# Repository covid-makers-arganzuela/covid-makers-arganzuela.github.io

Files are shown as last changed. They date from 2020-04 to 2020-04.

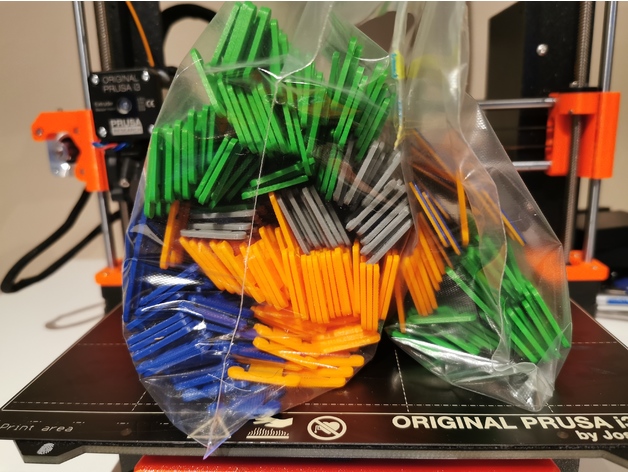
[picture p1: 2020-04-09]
modelos/salvaorejas/Surgical+Mask+Strap+Remix/images/IMG_20200330_075304.jpg

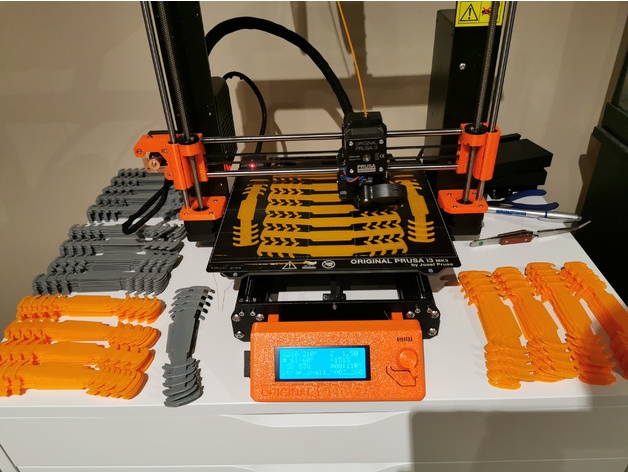
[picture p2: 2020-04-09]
modelos/salvaorejas/Surgical+Mask+Strap+Remix/images/IMG_20200330_213939.jpg

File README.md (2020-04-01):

# Grupo de Arganzuela de Coronavirus Makers

En este sitio mantenemos información útil para la coordinación del grupo de Arganzuela de [Coronavirus Makers](https://www.coronavirusmakers.org).

:tada: Canal de comunicación oficial: [grupo de Telegram](https://t.me/cov19arganzuela)

## Información de fabricación

* [Recomendaciones de ajustes de la impresora](ajustes.md): breve guía sobre
  cómo poner a punto la impresora antes de comenzar.

* [Modelos de visera](modelos/): modelos 3D de viseras utilizados por el grupo
  de Arganzuela. Dentro de los directorios se pueden encontrar configuraciones
  recomendadas para determinadas impresoras (archivos gcode y proyectos cuda
  personalizados).

## Colabora

Si tienes ajustes personalizados de impresión de alguno de los modelos puedes:
 * Si tienes permisos en este repositorio: 
   * haz el commit directamente
 * Si no tienes permisos en este repositorio o quires una revisión: 
   * haz una pull request en este repositorio
 * Si no sabes como hacer una pull request:
   * envía tus configuraciones (.gcode y proyecto Cura/Slicer .3MF/.MRML) al [grupo de Telegram](https://t.me/cov19arganzuela
)

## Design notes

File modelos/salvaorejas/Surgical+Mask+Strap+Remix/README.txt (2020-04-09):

Surgical Mask Strap Remix by Suraky on Thingiverse: https://www.thingiverse.com/thing:4249113

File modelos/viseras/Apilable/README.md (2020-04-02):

# Visera apilable (bescobarca)

Esta visera fue publicada por el usuario bescobarca en Thingverse. 

# Parámetros de impresión
Se recuerda que los parámetros pueden variar de unas impresoras a otras
 - Relleno: 60%
 - Soportes: no
 - Boquilla: 0.4 mm (**Es posible que no sirvan las de tamaño mayor**)
 - Material

# Licencia
Esta pieza se distribuye bajo una licencia CC-BY

# Enlaces
Pieza en Thingiverse: <https://www.thingiverse.com/thing:4251325>

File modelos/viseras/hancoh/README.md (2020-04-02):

# Visera Gregorio Marañón
Este modelo de visera es el disponible en la web de CoronavirusMakers. Su autor, como se indica en el PDF disponible, es  [Hanoch Hemmerich https://www.thingiverse.com/HanochH/about]

## Parámetros de impresión recomendados
Se recuerda que los parámetros pueden variar de unas impresoras a otras.

 - Diámetro del nozzle: 0.4mm
 - Altura de capa: 0.28mm
 - Relleno: 50%
 - Tipo de relleno: Rejilla
 - Capas superiores: 4
 - Capas inferiores: 2
 - Flujo: 80%
 - Sin soportes

 ### Velocidad de impresión:
 - Perímetros: 80mm/s
 - Perímetros pequeños: 80mm/s
 - Perímetros externos: 80mms/s
 - Relleno: 80mms/s
 - Relleno solido: 80mms/s
 - Relleno solido superior: 80mm/s
 - Puentes: 80mm/s
 - Relleno: 80mm/s
 - Recorrido: 180mm/s

 ### Material
  - PLA
 
 ## Enlaces
 - Publicación de la visera (zip): https://www.coronavirusmakers.org/index.php/es/documentos/category/7-d-i-y

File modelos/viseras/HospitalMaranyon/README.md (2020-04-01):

# Visera Gregorio Marañón
Este modelo de visera fue publicado por la Unidad de planificación avanzada y manufactura 3D del Hospital Gregorio Marañón, en su cuenta de twitter (@3d_maranon)

## Parámetros de impresión recomendados
 - Boquilla: 0.4mm a 0.8mm 
 - Altura de capa: 0.3mm 
 - Capas superiores e inferiores 3
 - Perímetros 3
 - Relleno 20%, triangular
 - Sin soporte
 - Velocidad de impresión: A elección del operador.
 
 ## Enlaces
 - Publicación de la visera: https://twitter.com/3d_maranon/status/1242177410759524355
 - Parámetros de impresión: https://twitter.com/3d_maranon/status/1242181121854582785

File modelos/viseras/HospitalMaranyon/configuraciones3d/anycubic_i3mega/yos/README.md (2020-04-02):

# Configuraciones

 - Temperatura capa inicial de la cama: 70
 - Temperatura capa inicial: 220
 - Velocidad capa inicial: 20 mm/s

Resto configuraciones por defecto

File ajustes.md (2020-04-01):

# Recomendaciones de ajustes de la impresora

(cortesía de Manel Ruiz)
 
En primer lugar, perded un poco de tiempo en ajustar la impresora, os evitará
dolores de cabez y tirar piezas a la basura (yo llevo unas cuantas). 
 
 * **Revisad la parte mecánica:** rodamientos, tensión de las correas de
   transmisión,... (hasta que apreté y ajusté bien todos los rodamientos,
   especialmente los de debajo de la cama, no desapareciero problemas que estaba
   intentando resolver cambiado ajustes SW) 
 
 * **Nivelación de la cama:** ha sido otro de mis grandes problemas. Revisadlo
   cada cierto tiempo si es necesario. 
 
 * **Calibrado:** hacedlo según se indica en
   https://covidmadrid.com/prueba-de-tolerancia/ Yo no lo hice del todo bien y
   he impreso unas cuantas visera cuya ranura es estrecha y no sé si podrá
   montarse la pantalla de PVC. Ahora tengo una expansión horizontal de -0,3 y
   queda de lujo. 
 
 * **Primera capa:** lo que mal empieza, mal acaba. Hasta que no he conseguido
   una buena primera capa todo han sido problemas. Lo que yo he hecho: 
   Subir la temperatura de la cama en la primera capa y después bajarla (ahora
   tengo 70º en la primera capa, 60º en el resto). Empecé con 75/70 y se pegaba
   bien la primera capa, pero después se abombaba la pared de la visera por el
   exceso de calor de la cama.  Subir la temperatura de impresión en la primera
   capa y después bajarla (yo ahora tengo 220º/215º) Bajar la velocidad de la
   primera capa. He terminado poniendo 20 mm/s para que la primera capa se fije
   bien a la cama. Resto de capas a 60 mm/s.

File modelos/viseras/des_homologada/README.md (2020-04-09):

# Visera del grupo covidmadrid

Estuvo homologada por la Comunidad de Madrid durante algunos días pero luego se
retiró la homologación. Dos tipos de impresión A (única) / B (partes) ambas con arandelas.

 * Ver ficha: https://covidmadrid.com/modelos-a-imprimir/
 
# Notas sobre la impresión

##Tetones para la parte frontal (Remache Frontal):
Probablemente necesitan escalado y ajustado

## Prueba de tolerancia
Se recomienda antes de imprimir el modelo realizar la prueba de tolerancia: https://covidmadrid.com/prueba-de-tolerancia/

## Ficheros STL
Para imprimir la visera hay dos opciones:
1. Imprimir el modelo A, que incluye la visera completa. Necesita una cama lo suficientemente grande. 
2. Imprimir el modelo B, que es el mismo que el modelo A, pero dividido en dos partes. Se deberá imprimir un fichero B1 y uno de los B2 (modelo con o sin hebilla). 

Independientemente de que se opte por imprimir el modelo A o el B, se necesiará también dos arandelas y los remaches que se consideren necesarios.

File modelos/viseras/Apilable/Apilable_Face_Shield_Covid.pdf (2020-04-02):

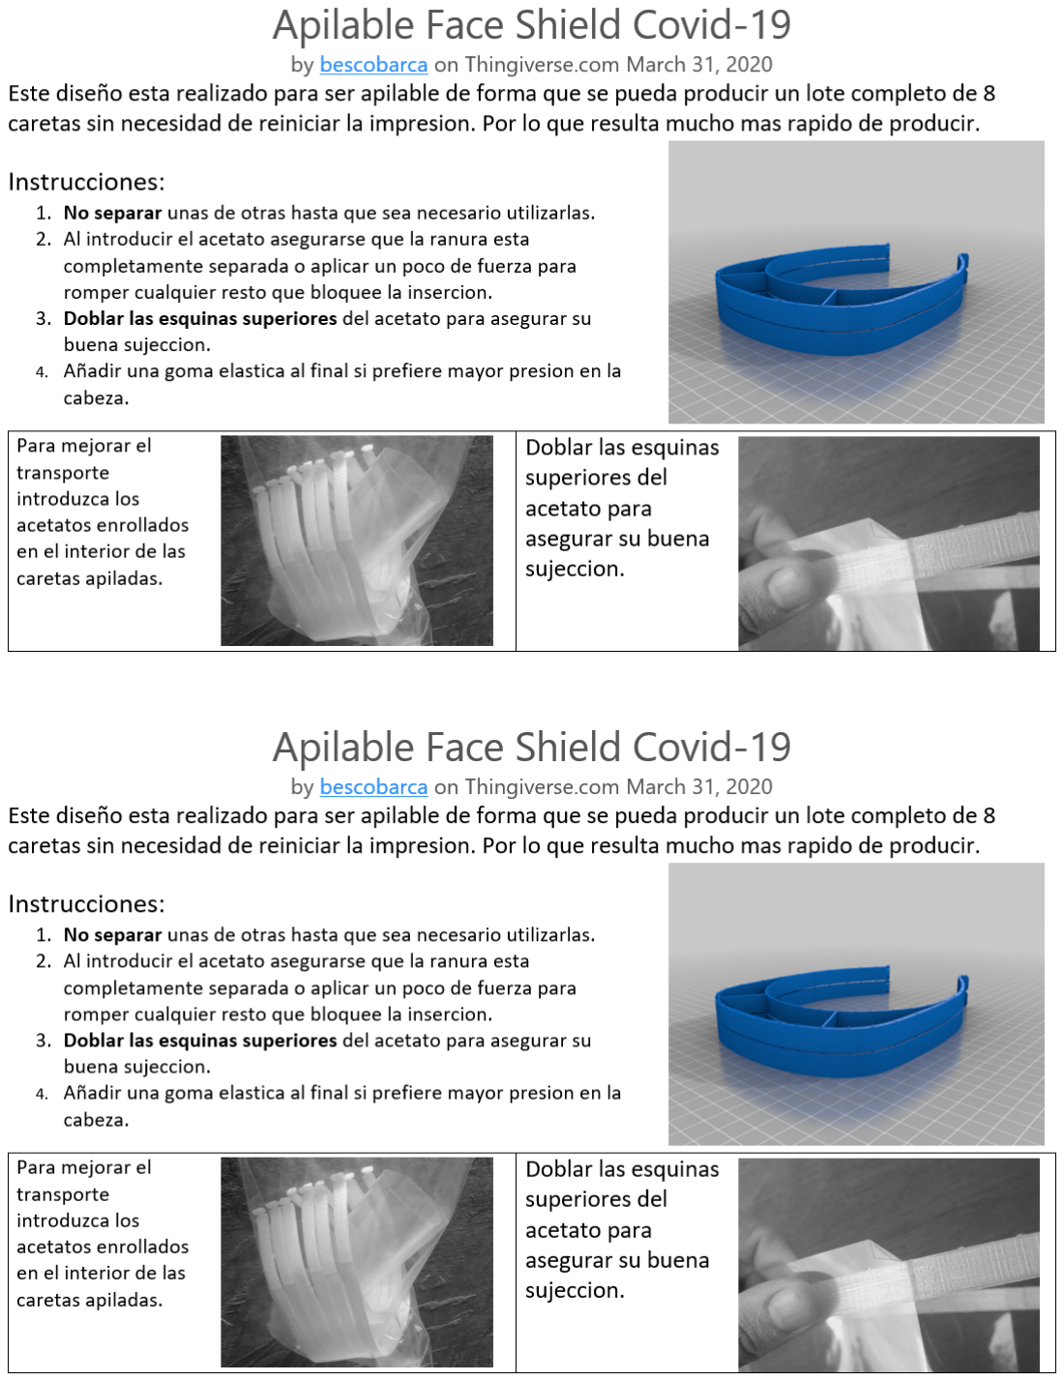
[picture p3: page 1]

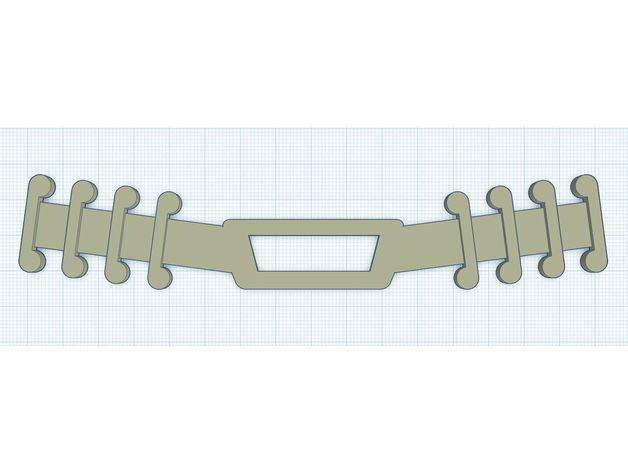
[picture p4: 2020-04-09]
modelos/salvaorejas/Surgical+Mask+Strap+Remix/images/strap-remix.JPG

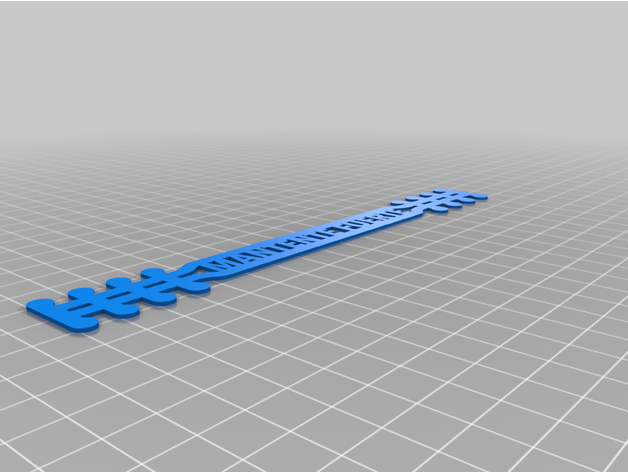
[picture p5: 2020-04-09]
modelos/salvaorejas/Salva+orejas+con+frases+/images/MANTENTE_FUERTE.png

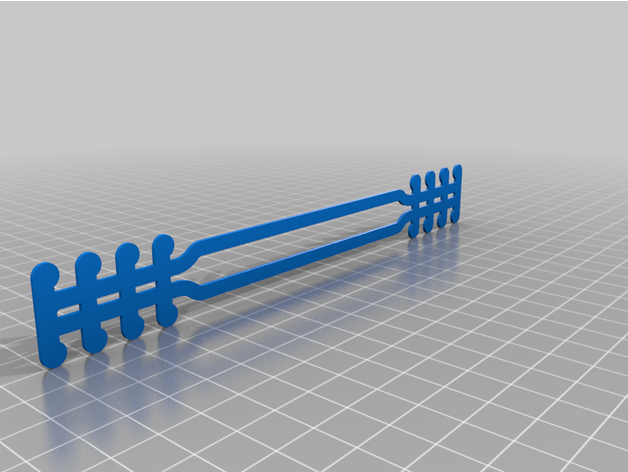
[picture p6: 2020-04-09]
modelos/salvaorejas/Salva+orejas+con+frases+/images/salva_orejas.png

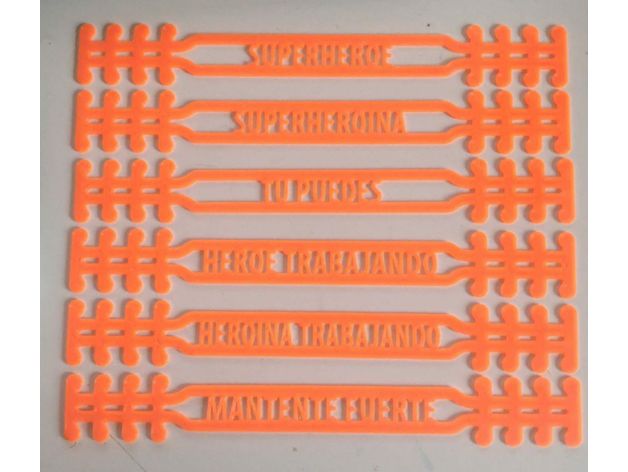
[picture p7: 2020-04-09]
modelos/salvaorejas/Salva+orejas+con+frases+/images/photo_2020-04-08_16.11.01.jpeg

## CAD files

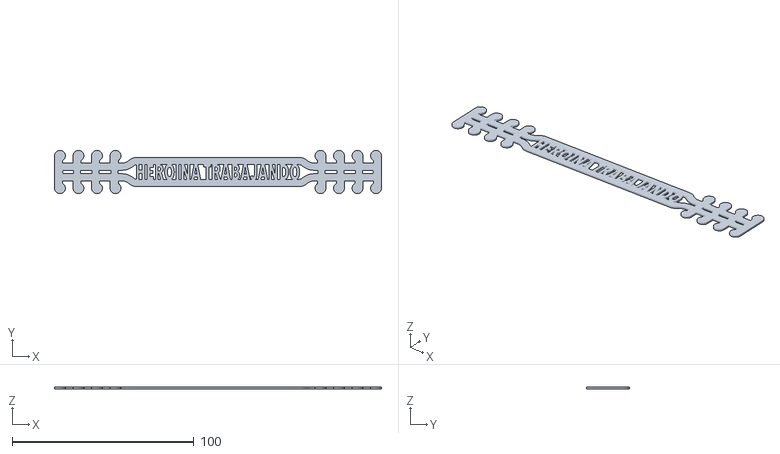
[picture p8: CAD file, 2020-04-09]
modelos/salvaorejas/Salva+orejas+con+frases+/files/HEROINA_TRABAJANDO.stl
180.0 x 23.8 x 1.00

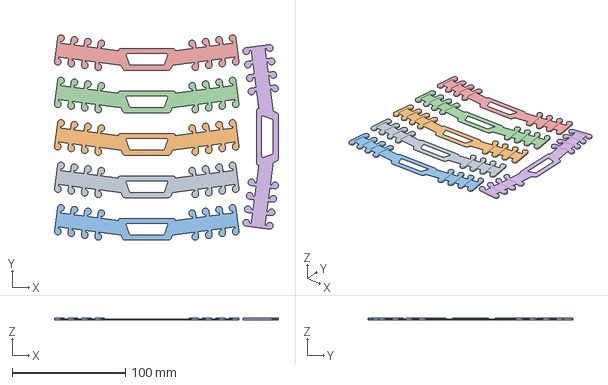
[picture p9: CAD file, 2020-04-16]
modelos/salvaorejas/Surgical+Mask+Strap+Remix/configuraciones3D/ender3/yonseca/Surgical_Mask_Strap_RemixPLA.3mf
197.9 x 181.5 x 2.00 mm

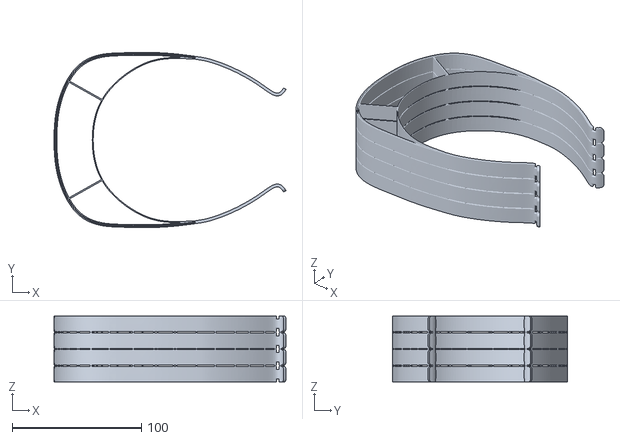
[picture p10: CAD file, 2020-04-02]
modelos/viseras/Apilable/4.stl
179.6 x 135.5 x 51.0

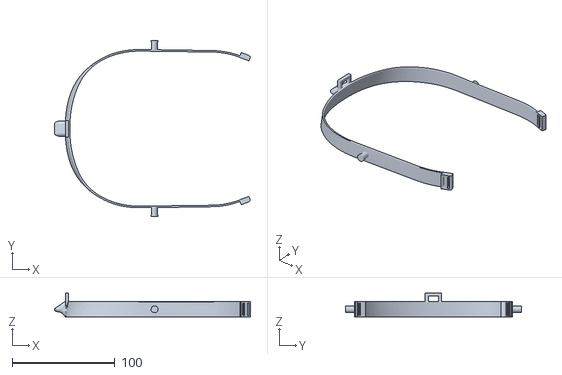
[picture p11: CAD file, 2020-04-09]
modelos/viseras/des_homologada/B2 Visera Madrid-Aprobada 1.0_CON HEBILLA.stl
190.9 x 171.2 x 23.3

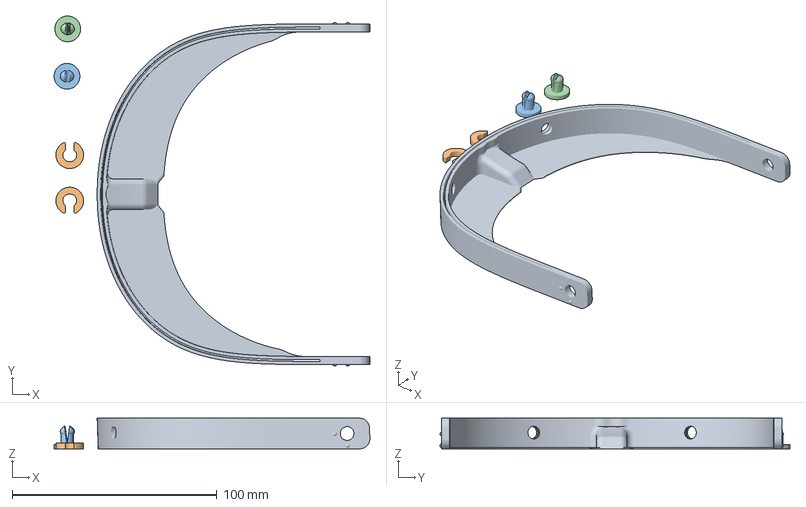
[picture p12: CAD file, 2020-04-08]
modelos/viseras/des_homologada/configuraciones3d/anycubic_i3mega/yos/AI3M_B1 Visera Madrid-Aprobada-arandela-tornillo 1.0.3mf
154.2 x 171.0 x 15.0 mm

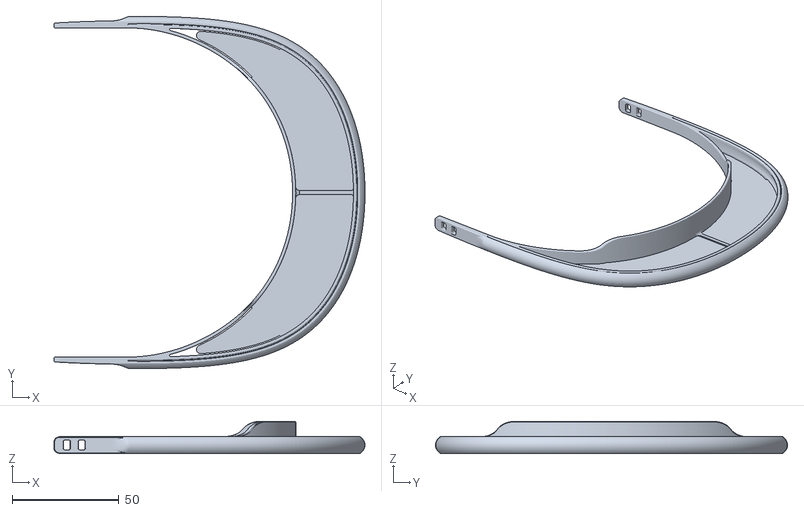
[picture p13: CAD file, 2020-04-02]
modelos/viseras/hancoh/Visera_Plana_con_cierre_y_ventilacion_0.5.stl
145.6 x 164.8 x 15.0

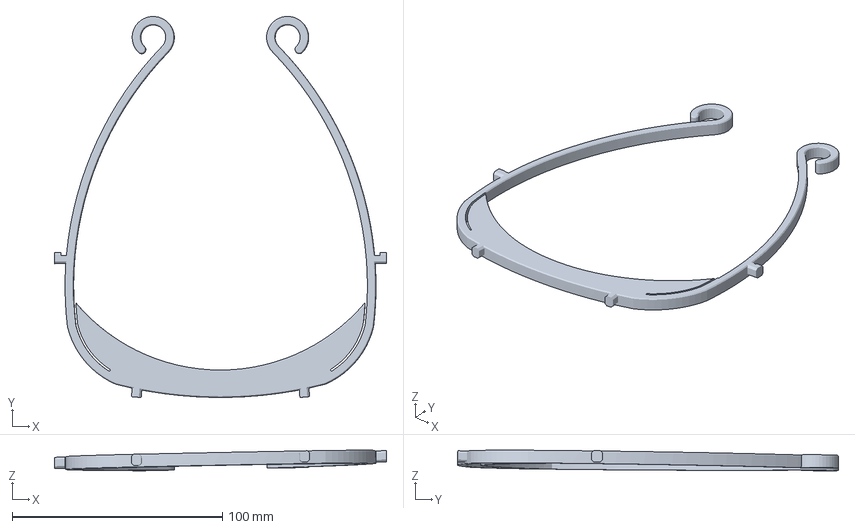
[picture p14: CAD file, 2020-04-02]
modelos/viseras/HospitalMaranyon/configuraciones3d/anycubic_i3mega/yos/AI3M_MARANYON.3mf
158.1 x 181.5 x 9.87 mm

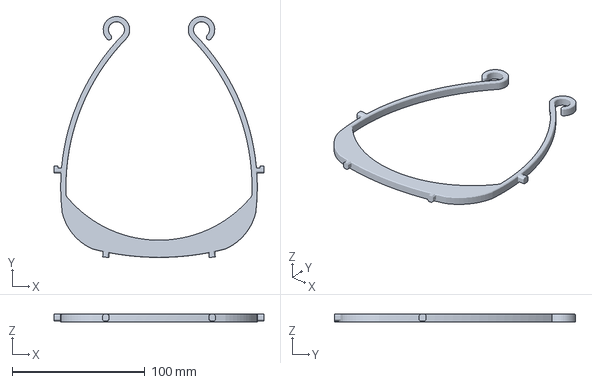
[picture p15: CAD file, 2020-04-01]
modelos/viseras/HospitalMaranyon/configuraciones3d/ender3/Yonseca/CE3_UPAM3D 01V1.3mf
158.0 x 181.4 x 6.00 mm

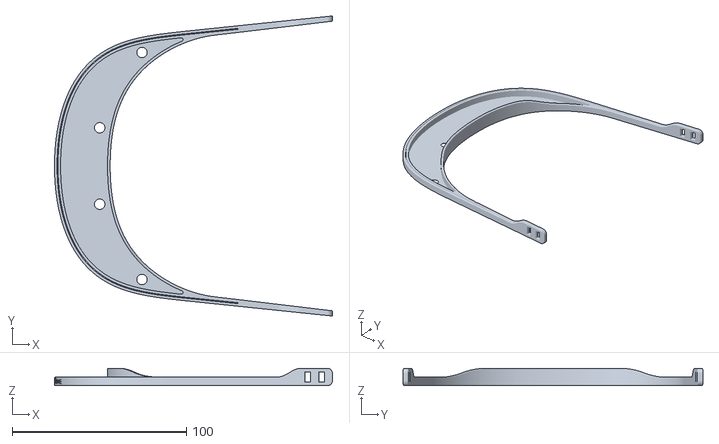
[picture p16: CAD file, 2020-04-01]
modelos/viseras/visera_plana/visera_plana_con_ventilacion.stl
159.8 x 172.4 x 10.0

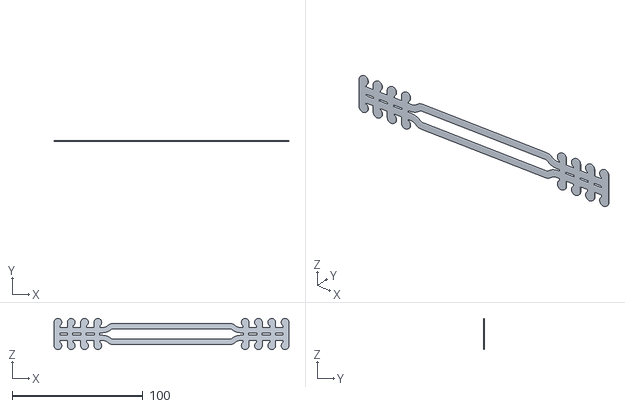
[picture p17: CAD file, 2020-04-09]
modelos/salvaorejas/Salva+orejas+con+frases+/files/salva_orejas.stl
180.0 x 1.06 x 23.8

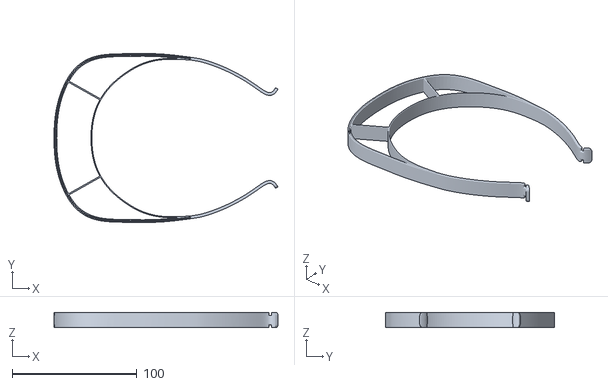
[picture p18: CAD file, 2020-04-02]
modelos/viseras/Apilable/1.stl
179.6 x 135.5 x 12.0

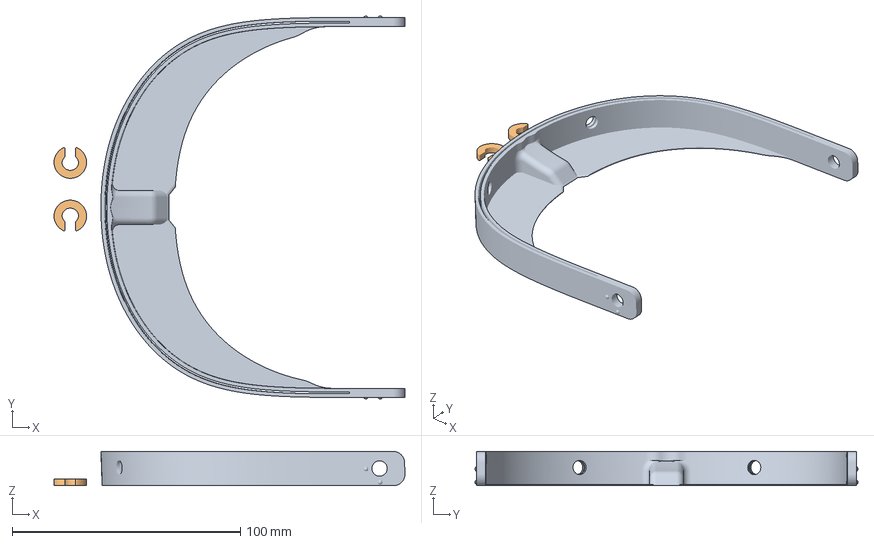
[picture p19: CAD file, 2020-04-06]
modelos/viseras/des_homologada/configuraciones3d/anycubic_i3mega/yos/AI3M_B1 Visera Madrid-Aprobada 1.0.3mf
153.7 x 167.8 x 15.0 mm

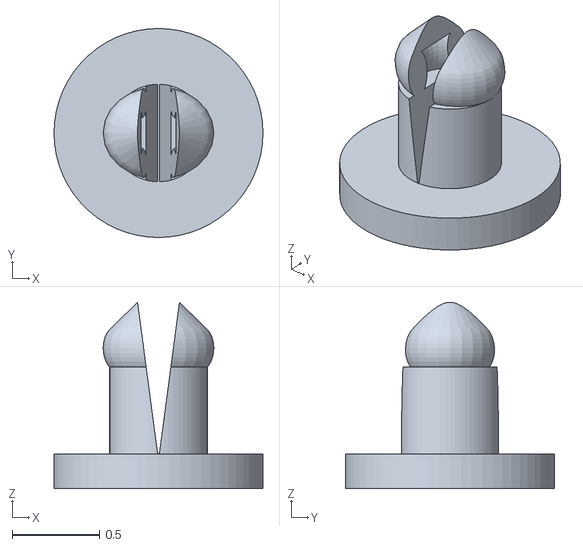
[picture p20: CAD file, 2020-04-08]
modelos/viseras/des_homologada/Remache frontal.STL
1.20 x 1.20 x 1.07

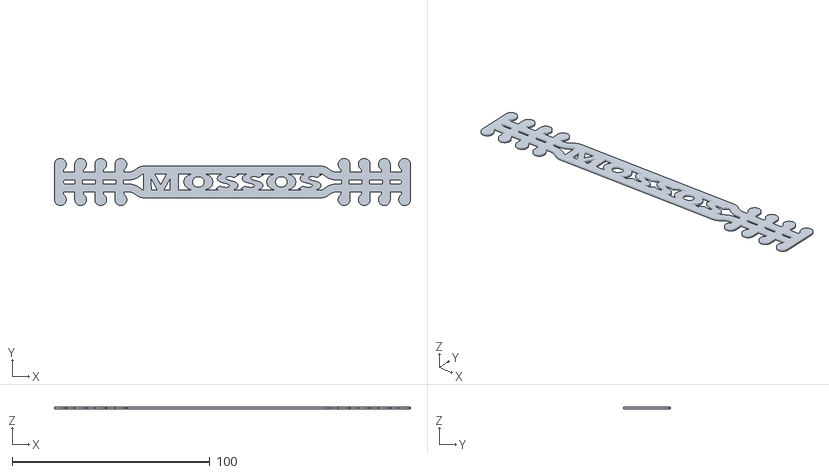
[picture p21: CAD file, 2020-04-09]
modelos/salvaorejas/Salva+orejas+con+frases+/files/MOSSOS.stl
180.0 x 23.8 x 1.00

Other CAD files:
modelos/salvaorejas/Surgical+Mask+Strap+Remix/files/Surgical_Mask_Strap_Remix.3mf
modelos/viseras/HospitalMaranyon/UPAM3D 01V1.stl
modelos/viseras/Apilable/2.stl
modelos/viseras/des_homologada/B1 Visera Madrid-Aprobada 1.0.stl
modelos/salvaorejas/Salva+orejas+con+frases+/files/ERES_GRANDE.stl
modelos/salvaorejas/Salva+orejas+con+frases+/files/FURA_3.stl
modelos/salvaorejas/Salva+orejas+con+frases+/files/HEROE_TRABAJANDO.stl
modelos/salvaorejas/Salva+orejas+con+frases+/files/MANTENTE_FUERTE.stl
modelos/salvaorejas/Salva+orejas+con+frases+/files/SUPERHEROE.stl
modelos/salvaorejas/Salva+orejas+con+frases+/files/SUPERHEROINA.stl
modelos/salvaorejas/Salva+orejas+con+frases+/files/TU_PUEDES.stl
modelos/salvaorejas/Surgical+Mask+Strap+Remix/files/Surgical_Mask_Strap_Remix.stl
modelos/viseras/des_homologada/A -Principal Visera Madrid-Aprobada 1.0.stl
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

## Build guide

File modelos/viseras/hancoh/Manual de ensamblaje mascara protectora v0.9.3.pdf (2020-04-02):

# Manual de impresión y ensamblaje mascara

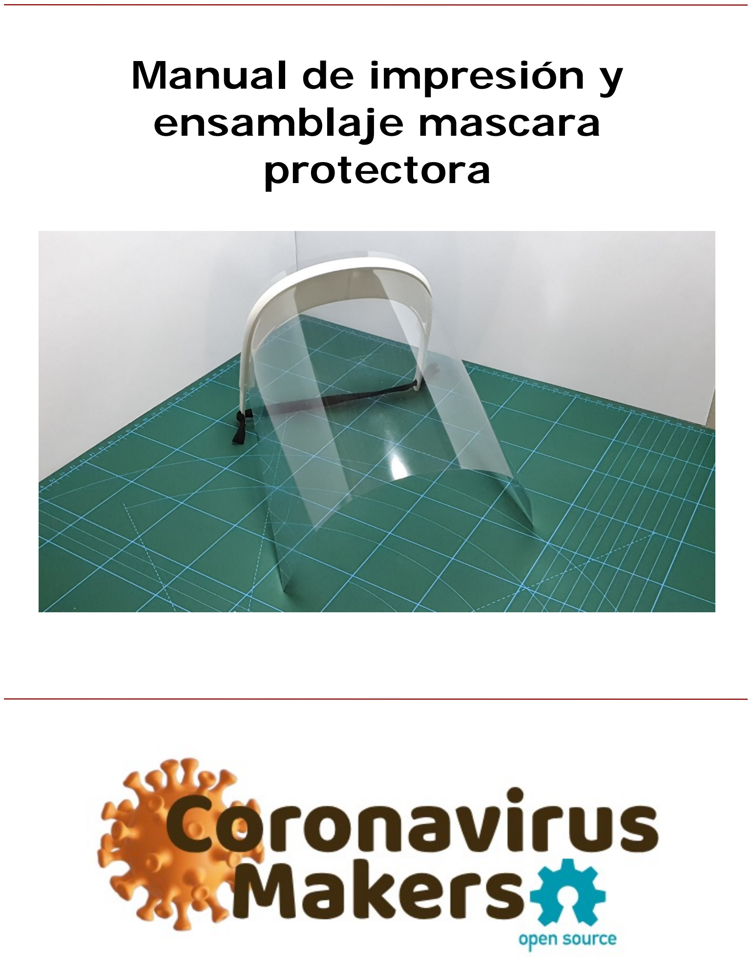
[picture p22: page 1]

# protectora

www.coronavirusmakers.org | Página: 2/18

# Datos del Documento

Autor: | @YKA3D
Revisor: | @kermithenson
Fecha de publicación: | 18/03/2020
Observaciones:
Para comenzar a fabricar es necesario que la máquina esté correctamente calibrada. Una vez calibrada, se deberá llevar a cabo una prueba de tolerancia.

Test: https://www.thingiverse.com/thing:1662342

# Hoja de Cambios

Fecha | Versión | Autor | Cambios
18 de marzo de 2020 | v.0.1 | @YKA3D | Creación del documento
18 de marzo de 2020 | V.0.3 | @kermithenson | Modificación protocolos
20 de marzo de 2020 | V.0.9 | @YKA3D | Actualizaciones varias

# Versión STL

Fecha | Versión | Autor | Cambios
20 de marzo de 2020 | v.0.3 | @Hanochh | Creación STL mascara
22 de marzo de 2020 | V.0.5 | @Hanochh | Adaptaciones varias

# Índice

### Introducción

El siguiente manual explica el procedimiento por el cual se realiza la fabricación mediante FDM y el posterior ensamblaje de las máscaras de protección diseñadas por la comunidad Coronavirus Maker en España dentro de la crisis de COVID-19.

Los dispositivos constan de 2 partes: la sujeción (impresa en PLA) y la lámina de protección (lámina de PVC).

El autor del diseño es Hanoch Hemmerich. (https://www.thingiverse.com/HanochH/about)

El objetivo de esta ayuda no es una solución para evitar contagios, sino que su finalidad es alargar la vida de los sistemas EPI homologados del personal sanitario y no sanitario que se halla frente a posibles portadores o infectados, que ya es facilitado por el departamento de Riesgos Laborales de sus respectivas organizaciones.

La lamina utilizada es de PVC de tamaño DINA4 y colocada en formato apaisado (horizontal) con el objetivo de cubrir la cara lo más ampliamente posible.

El sistema de colocación está diseñado para que sea fácil y rápido de colocar y retirar. Así mismo, este sistema permite su ajuste según el perímetro craneal de cada individuo. Adicionalmente, el presente dispositivo, dispone de 2 ranuras que evitan la formación de vaho por el usuario al respirar, garantizando la máxima visibilidad en todo momento.

Por motivos de bioseguridad, y siguiendo la normativa, este sistema está diseñado para un solo uso. No obstante, puede ser desinfectados mediante métodos químicos bajo el criterio del equipo de Riesgos Laborales. En ningún caso debe esterilizarse por métodos físicos o químicos. En caso de requerir su desinfección, se ha testado con una solución acuosa de hipoclorito sódico al 5%.

Desde Coronavirus Maker insistimos que es criterio del centro la reutilización del dispositivo. Este equipo está diseñado para usar y tirar, a pesar de ser material reciclable.

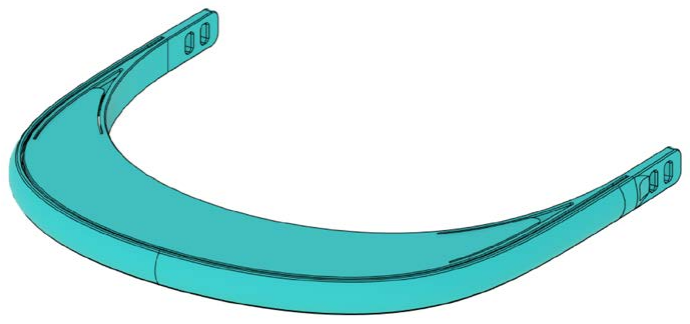
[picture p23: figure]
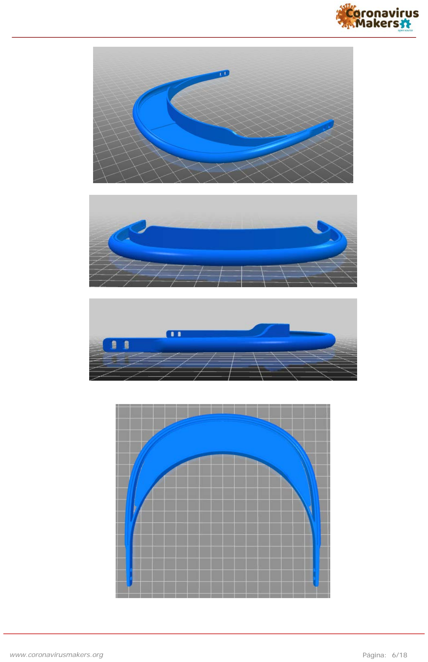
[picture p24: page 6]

### Materiales

Los siguientes enlaces solo son una referencia del material utilizado para la elaboración de las pantallas protectoras.

- Lamina frontal
- Láminas de PVC tamaño DINA4
- Opcionalmente:
- Láminas de acetato de 180 o 240 micras.
- Laminas PET de 400 micras
- Correa posterior
- Goma elástica o similar

### Parámetros de impresión

El archivo para su impresión se puede descargar desde el siguiente enlace:

TEMPORAL: https://www.thingiverse.com/thing:4233193/

Los parámetros de impresión solo son una guía de referencia, dado que cada impresora tiene sus propios parámetros para garantizar impresiones optimas.

- Diámetro del nozzle: 0.4mm
- Altura de capa: 0.28mm
- Relleno: 50%
- Tipo de relleno: Rejilla
- Capas superiores: 4
- Capas inferiores: 2
- Flujo: 80%
- Sin soportes
- Velocidad de impresión:
- Perímetros: 80mm/s
- Perímetros pequeños: 80mm/s
- Perímetros externos: 80mms/s
- Relleno: 80mms/s
- Relleno solido: 80mms/s
- Relleno solido superior: 80mm/s
- Puentes: 80mm/s
- Relleno: 80mm/s
- Recorrido: 180mm/s

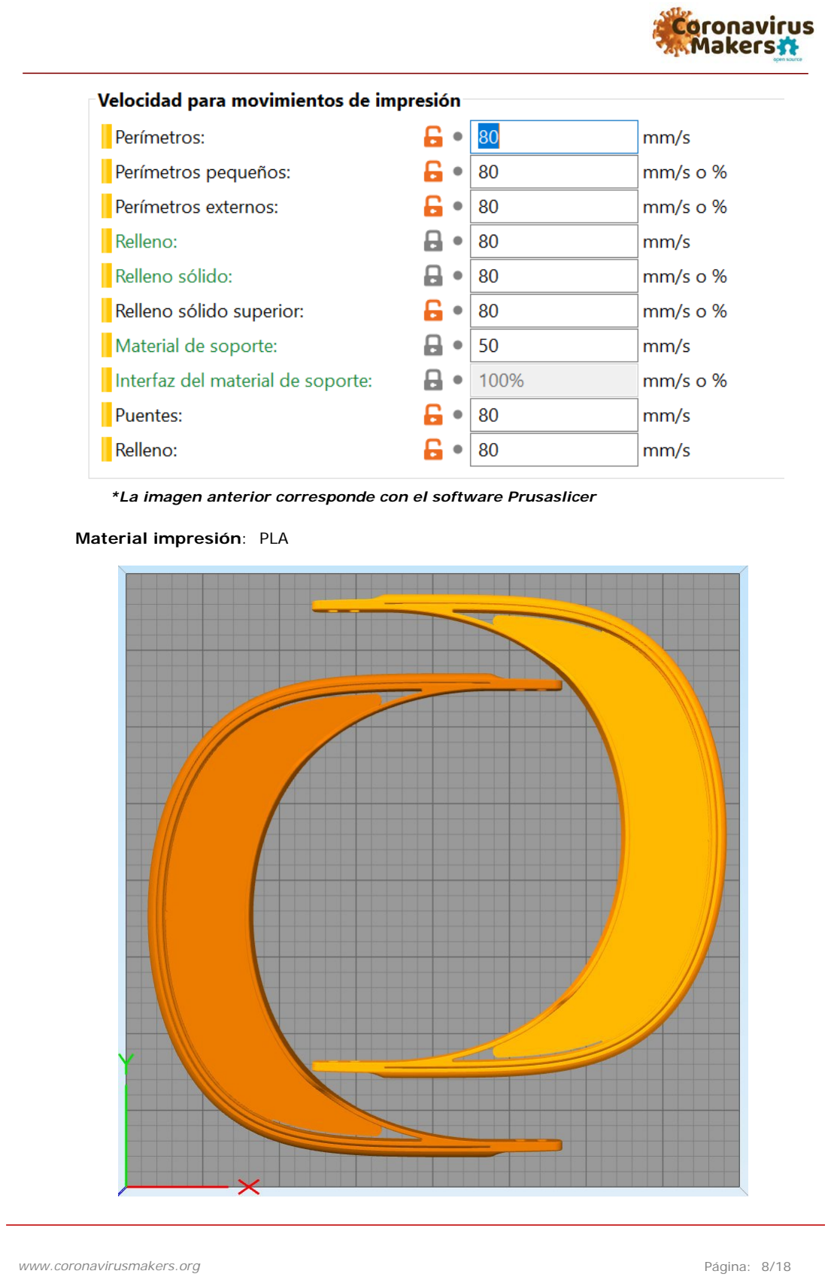
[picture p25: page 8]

*La imagen anterior corresponde con el software Prusaslicer

Material impresión: PLA

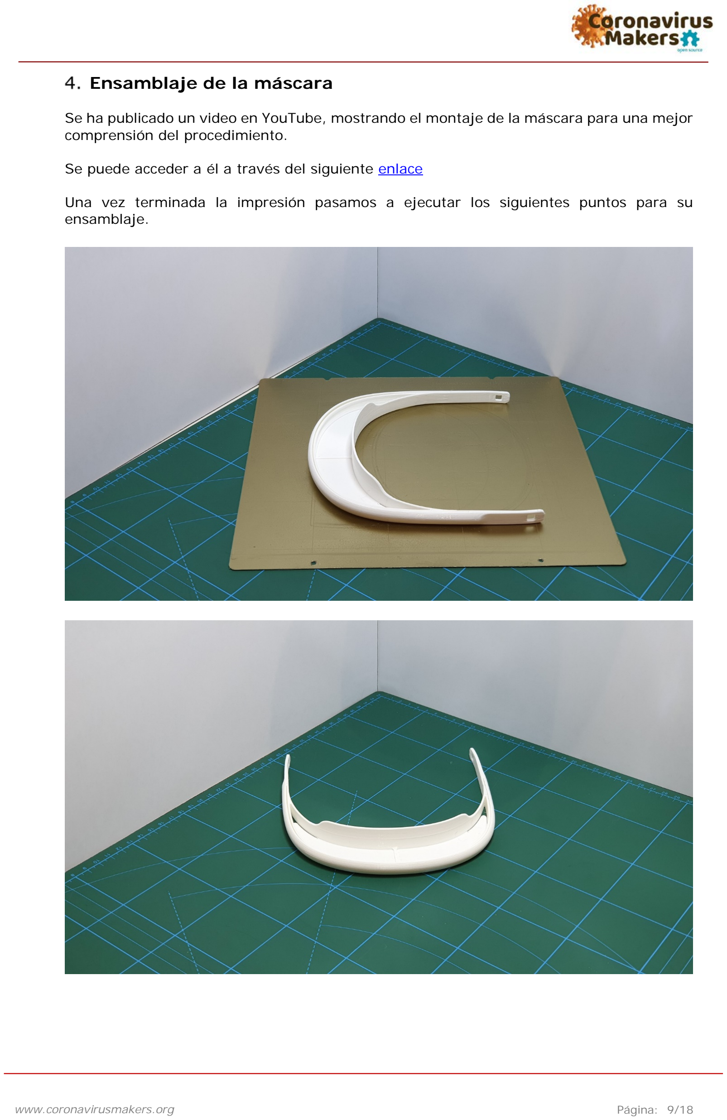
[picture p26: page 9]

### Ensamblaje de la máscara

Se ha publicado un video en YouTube, mostrando el montaje de la máscara para una mejor comprensión del procedimiento.

Se puede acceder a él a través del siguiente enlace (https://www.youtube.com/watch?v=xsc1RIfQK8s)

Una vez terminada la impresión pasamos a ejecutar los siguientes puntos para su ensamblaje.

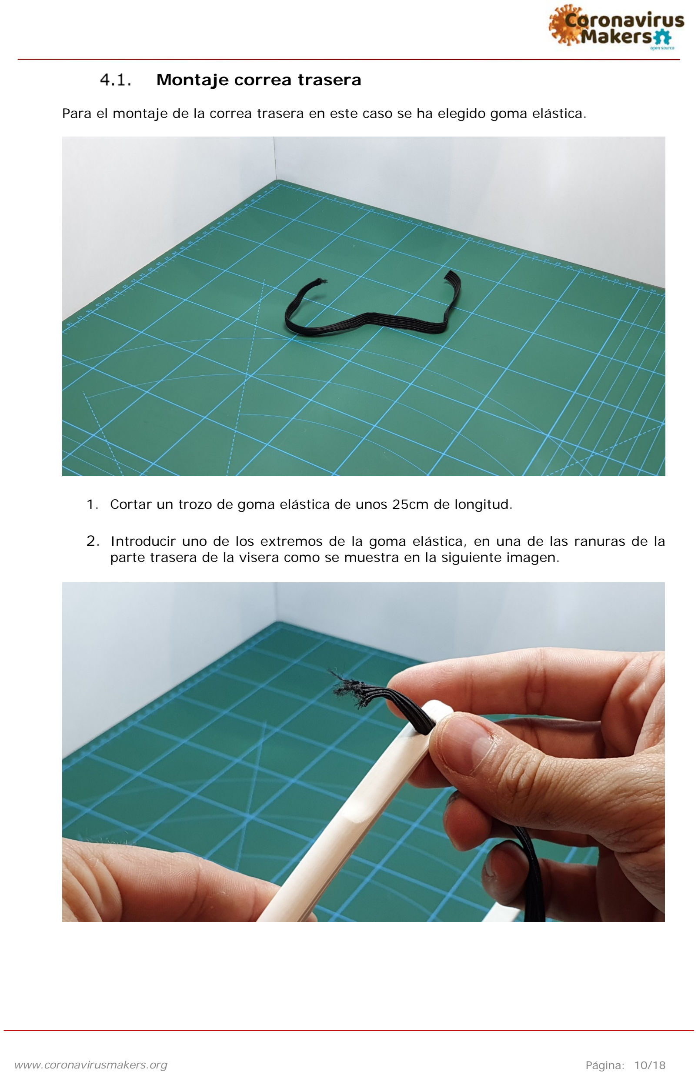
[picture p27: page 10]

### Montaje correa trasera

Para el montaje de la correa trasera en este caso se ha elegido goma elástica.

1. Cortar un trozo de goma elástica de unos 25cm de longitud.
2. Introducir uno de los extremos de la goma elástica, en una de las ranuras de la parte trasera de la visera como se muestra en la siguiente imagen.

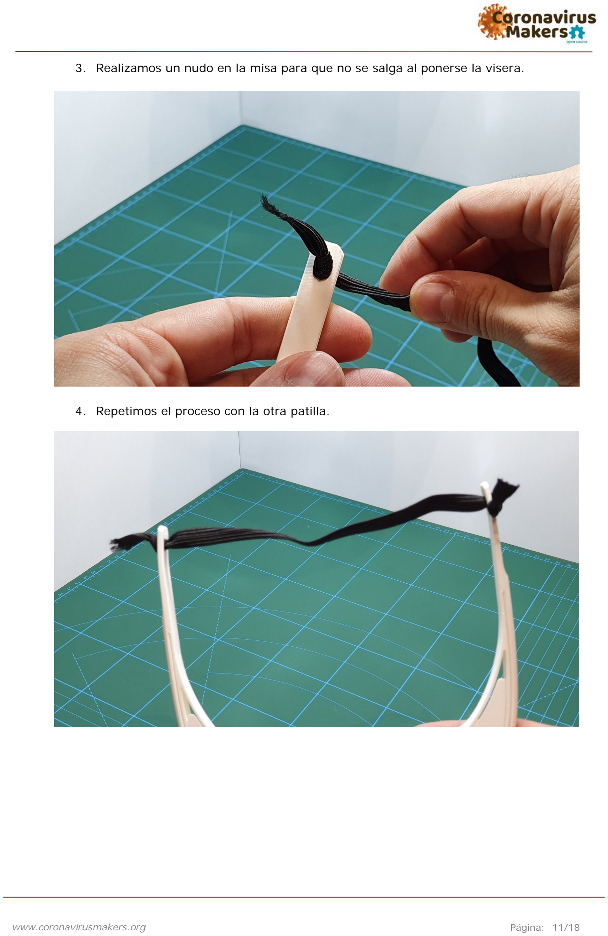
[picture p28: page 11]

3. Realizamos un nudo en la misa para que no se salga al ponerse la visera.
4. Repetimos el proceso con la otra patilla.

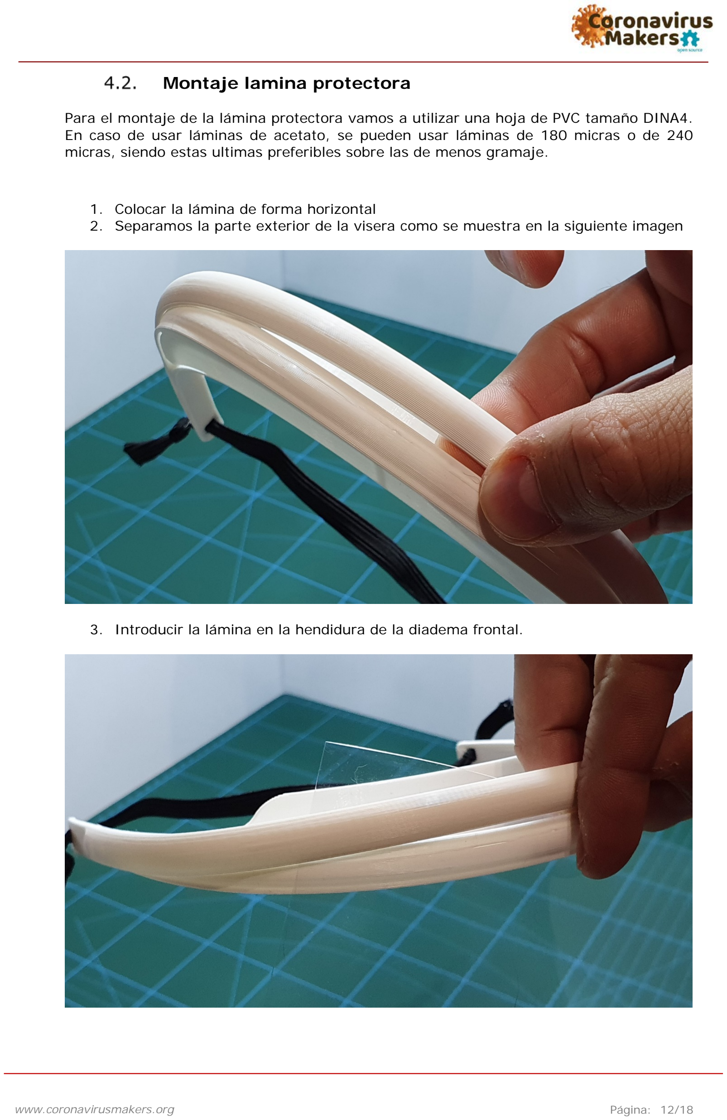
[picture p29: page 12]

### Montaje lamina protectora

Para el montaje de la lámina protectora vamos a utilizar una hoja de PVC tamaño DINA4. En caso de usar láminas de acetato, se pueden usar láminas de 180 micras o de 240 micras, siendo estas ultimas preferibles sobre las de menos gramaje.

1. Colocar la lámina de forma horizontal
2. Separamos la parte exterior de la visera como se muestra en la siguiente imagen
3. Introducir la lámina en la hendidura de la diadema frontal.

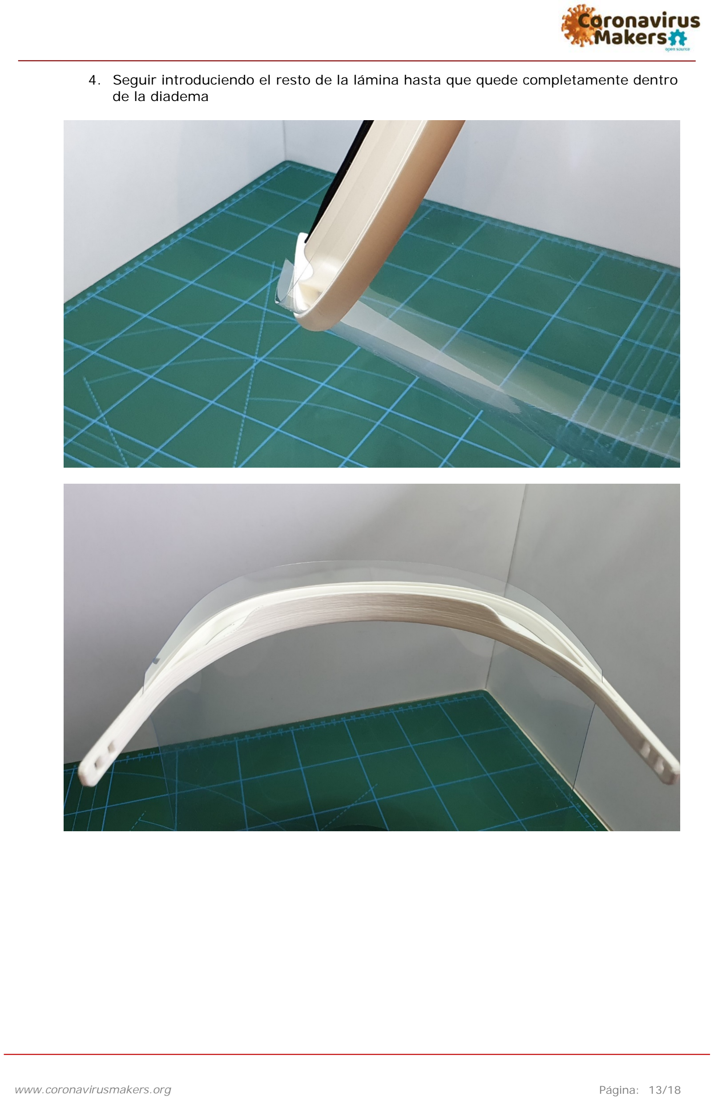
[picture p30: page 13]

4. Seguir introduciendo el resto de la lámina hasta que quede completamente dentro de la diadema

5. Una vez introducida por completo bajamos la parte exterior de la diadema para que queda la lámina bien fijada

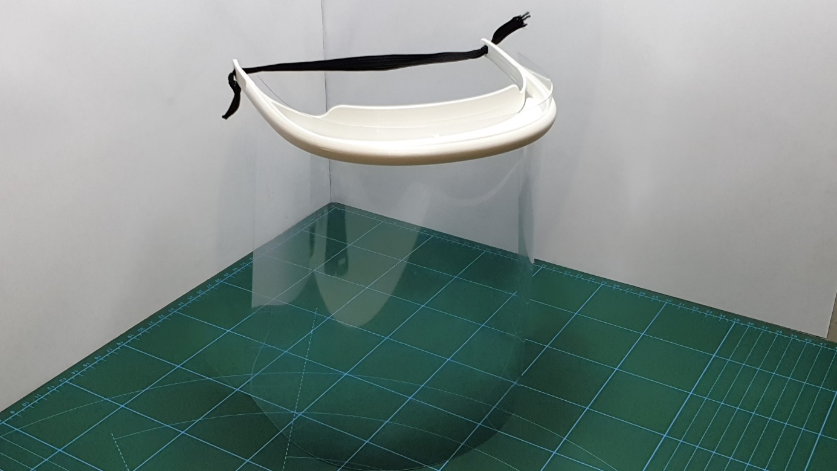
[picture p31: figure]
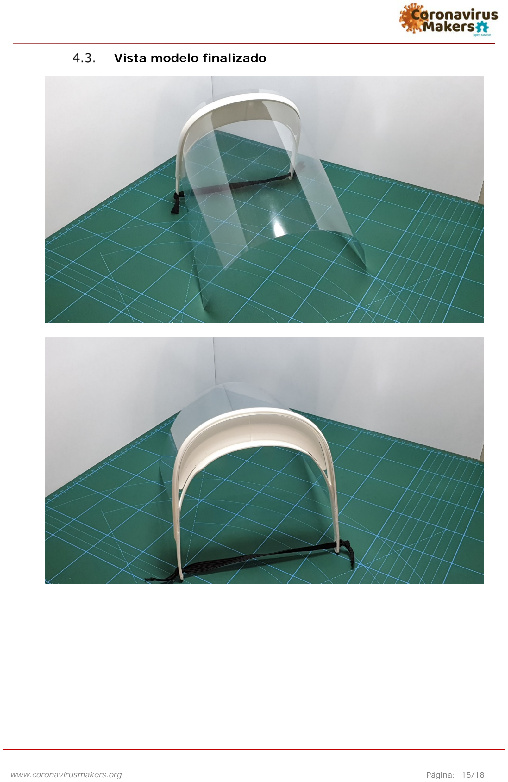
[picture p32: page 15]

### Vista modelo finalizado

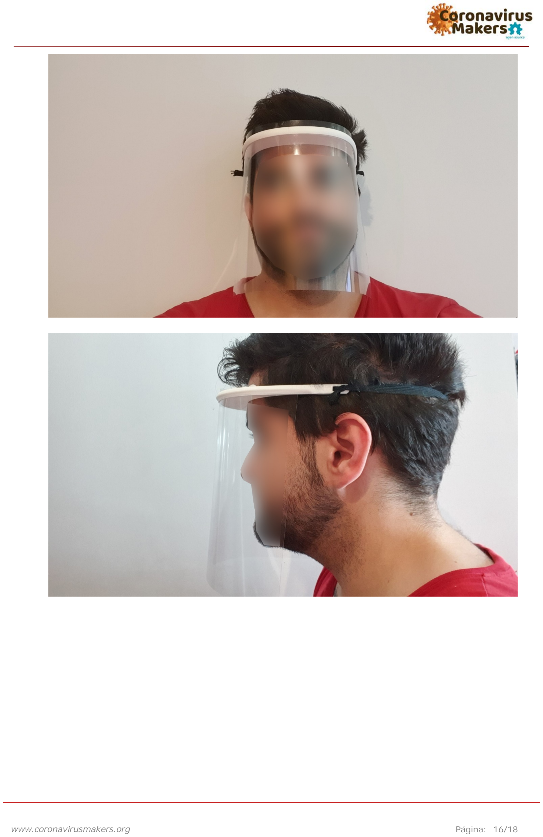
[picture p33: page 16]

En caso de usar una cinta no elástica, el resultado debe ser similar a la siguiente imagen:

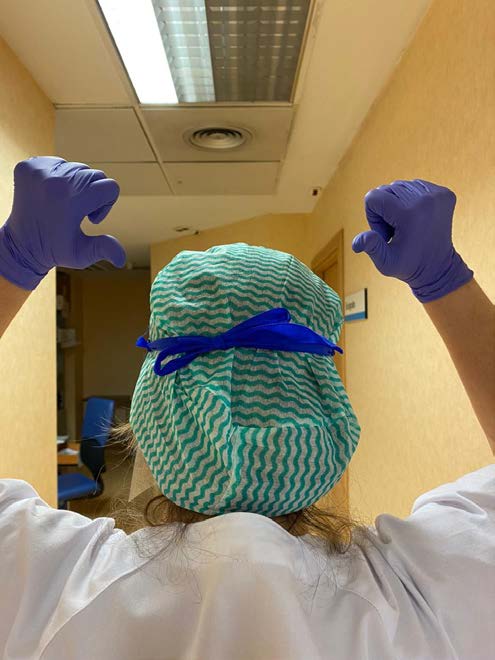
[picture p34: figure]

### Higienización

### [TO DO]

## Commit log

2020-04-01 Prototipo para organizacion
    [visera_plana_con_ventilacion.stl]
2020-04-01 Descripcion de ajustes
2020-04-01 Visera covidmadrid
    [A -Principal Visera Madrid-Aprobada 1.0.stl, Arandelas Visera Madrid-Aprobada 1.0.stl, B1 Visera Madrid-Aprobada 1.0.stl, B2 Visera Madrid-Aprobada 1.0.stl]
2020-04-01 eliminar mensaje de prototipo
2020-04-01 mejoras en el README
2020-04-01 Incluir cómo ajustar la impresora
2020-04-01 Listado de modelos para la web estática
2020-04-01 Añado la visera del Gregorio Marañón
    [UPAM3D 01V1.stl]
2020-04-01 Quito eñes y añado gcode y 3mf de Cura para la Ender 3
    [CE3_UPAM3D 01V1.3mf, UPAM3D 01V1.stl]
2020-04-01 Reorganización ficheros de Yonseca
    [CE3_UPAM3D 01V1.3mf, UPAM3D 01V1.stl]
2020-04-02 Añado el modelo Hancoh
    [Visera_Plana_con_cierre_y_ventilacion_0.5.stl]
2020-04-02 Añadida la configuración para marañon
    [AI3M_MARANYON.3mf]
2020-04-02 Añado readme para la visera Hancoh
2020-04-02 Añado visera apilable
    [1.stl, 2.stl, 4.stl]
2020-04-03 Configuraciones para covidmadrid
    [AI3M_B1 Visera Madrid-Aprobada 1.0.3mf, AI3M_B2 Visera Madrid-Aprobada 1.0.3mf]
2020-04-04 Añado ajustes para la visera homologada
    [CE3_Arandelas Visera Madrid-Aprobada 1.0.3mf]
2020-04-04 Revert "Añado ajustes para la visera homologada"
    This reverts commit e59b842f02e79ca31ae414e260ac9d43581dc0fd.
    [CE3_Arandelas Visera Madrid-Aprobada 1.0.3mf]
2020-04-06 Incluir arandelas en B1
    [AI3M_B1 Visera Madrid-Aprobada 1.0.3mf]
2020-04-08 Añadido tetones
    [Remache frontal.STL]
2020-04-08 Cambiar nombre para mejorar claridad
    [A -Principal Visera Madrid-Aprobada 1.0.stl, AI3M_B1 Visera Madrid-Aprobada 1.0.3mf, AI3M_B2 Visera Madrid-Aprobada 1.0.3mf, Arandelas Visera Madrid-Aprobada 1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]
2020-04-08 Configuracion con arandelas y tornillos
    [AI3M_B1 Visera Madrid-Aprobada-arandela-tornillo 1.0.3mf]
2020-04-09 Añado visera des-homologada con hebilla
    [B2 Visera Madrid-Aprobada 1.0_CON HEBILLA.stl]
2020-04-09 Añado salvaorejas
    [1.stl, 2.stl, 4.stl, A -Principal Visera Madrid-Aprobada 1.0.stl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]
2020-04-16 Añado salvaorejas y configuración
    [Surgical_Mask_Strap_Remix.3mf, Surgical_Mask_Strap_RemixPLA.3mf]
